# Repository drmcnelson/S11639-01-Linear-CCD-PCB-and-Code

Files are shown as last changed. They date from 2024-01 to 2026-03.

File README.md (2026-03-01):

# S11639-01-Linear-CCD-PCB-and-Code

By Dr M. C. Nelson, Copyright 2020-2025

Original repository [github.com/drmcnelson/S11639-01-Linear-CCD-PCB-and-Code](https://github.com/drmcnelson/S11639-01-Linear-CCD-PCB-and-Code)

This repo provides electronics, firmware and host software for the Hamamatsu S11639-01, a linear CCD sensor that has high sensitivity at 1300V/lx s and low dark noise at 0.2mV (for a 10msec exposure).  With saturation at 2V, the dynamic range is 10,000.
The electrical design is implemented as a two board set, sensor and controller, for mechanical stability and interchangeability.
The sensor board has the socketed sensor, logic gates to drive the pins, and a low noise all differential analog section with a high precision differential 16 bit ADC.
The controller operates the sensor and interacts with a host computer over USB, and has pins for trigger, gate, sync and busy signals.
The command interface is human readable ascii, data transfers are selectable in ascii or binary.

N.B.  This is an update to bring the S11639-0 board into compatibility with the new connector layout for our controller boards.   This design is not yet built, sponsors are welcome.  Please click the sponsor button at the top of the page.

*The original boards and their matching controllers are in the subdirecty labeled [Rev0Boards](./Rev0Boards).*

This version of the board is designed to be used with either of the our controllers, the [Teensy 4.0 based controller](https://github.com/drmcnelson/SPI-Instrumentation-Controller-T4.0) 
and the [Teensy 4.1 based controller](https://github.com/drmcnelson/SPI-Instrumentation-Controller-T4.1).
In principle, the S11639-01 could be used with a number of different Arduino boards.  After some extensive and detailed testing, we prefer the Teensy 4.x boards.  These have good implementations for 16 bit transfers over SPI and they have 480MHz USB for fast transfers to the host computer.

The firmware, which runs in the controller, provides high end functionality including clocked, triggered, and gated operation.
In the firmware, codes that are specific to the sensor are in a separate c++ file and header.  The "sketch file" implements a command interface and calls the sensor code to do the "work" of collecting frames in various operating modes.  The codes throughout, use the standard Arduino libraries plus a small number of optional register level enhancements for the i.MX RT MCU that provide faster and more constant interrupt latency and SPI transfers with less overhead.

## Sensor board details
The following image shows the circuit side of the sensor board with the high precision low noise differential front end (dual opamp lower right, adjacent to the video out pin from the sensor) interfaced to a differential 16bit 1MSPS ADC, and logic level converters (center) for the external digital interface.
The sensor is socketed on the reverse side. 
SPI and logic signals are brought to the double row header at the top edge of the board (ribbon cable compatible).
The external logic level is set by VDD supplied by the controller card.
Power for the sensor and other circuit elements is 5V and supplied by a separate connector.
The small jumper top center near the double row header, selects whether the CNVST pin on the ADC is connected to the TRG signal from the sensor or to the host processor.
(The firmware at present assumes the CNVST pin is connected to the MCU.)
The jumper and header (lower left) selects the internal 4.096V reference or provides a connector for an external reference.
The output from the analog section is available on the three pin header center bottom.
The trim pot should be set to 1.6V for sensors meeting the "typical" spec with output from 0.6V to 2.6V, there is a test point next to the trim pot labeled Voffset where the offset voltage can be measured.

<p align="center">
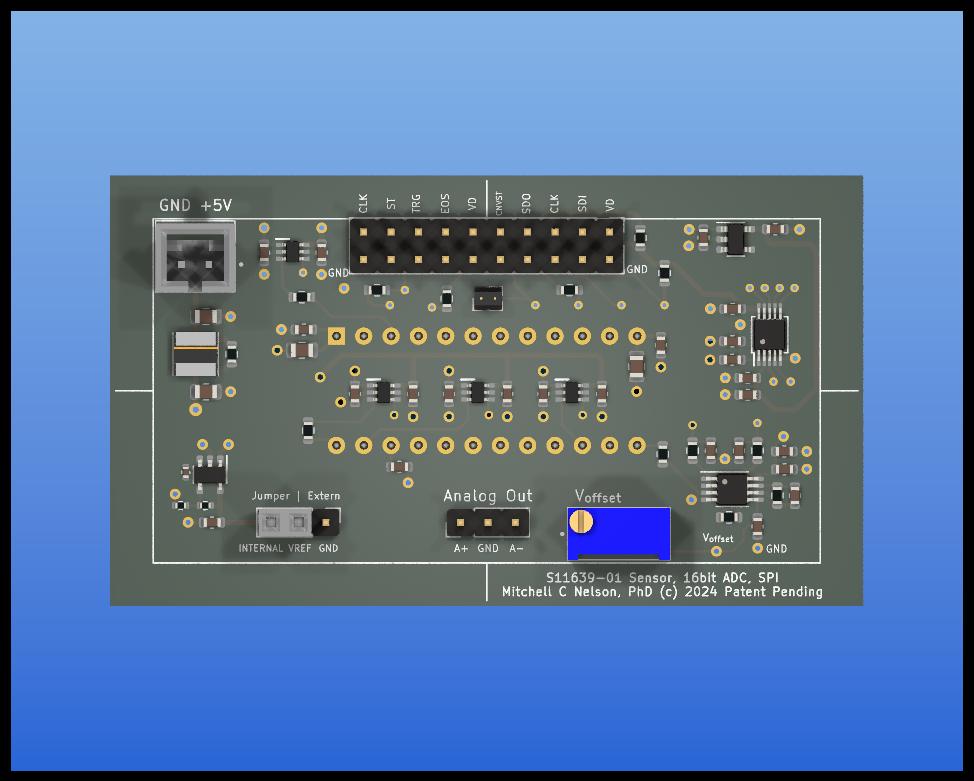
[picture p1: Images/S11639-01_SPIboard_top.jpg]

</p>

<p align="center">
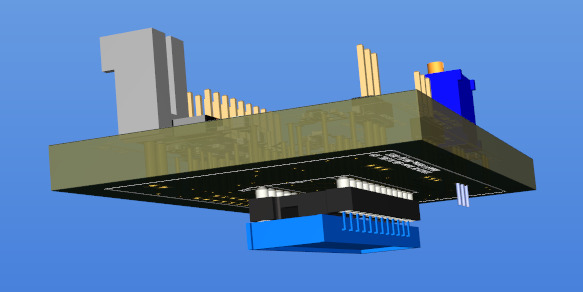
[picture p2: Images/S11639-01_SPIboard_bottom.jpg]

</p>

## T4.0 Controller board details
Please refer to the repo at 
The following describes the T4.0 based controller. The double row header across the top matches that on the sensor board.  The two boards should be connected by a ribbon cable that can be a few inches in length, and by a two wire cable for power, between the connectors labeled "5V" upper left on this board and upper left on the sensor board.  (The power cable will cross over the ribbon cable when the boards are positioned correctly and joined by a ribbon cable.)
The single row headers provides access to the digital interface signals and provides additional pins to the right for a trigger input, sync and busy ouputs and spare digital I/O pin.   The double row header on the left provides access to the onboard analog digital converters and any of these can be used for digitial I/O.  While all of these have diode protection, users should be cognizant that the Teensy is not 5V tolerant. 

<p align="center">
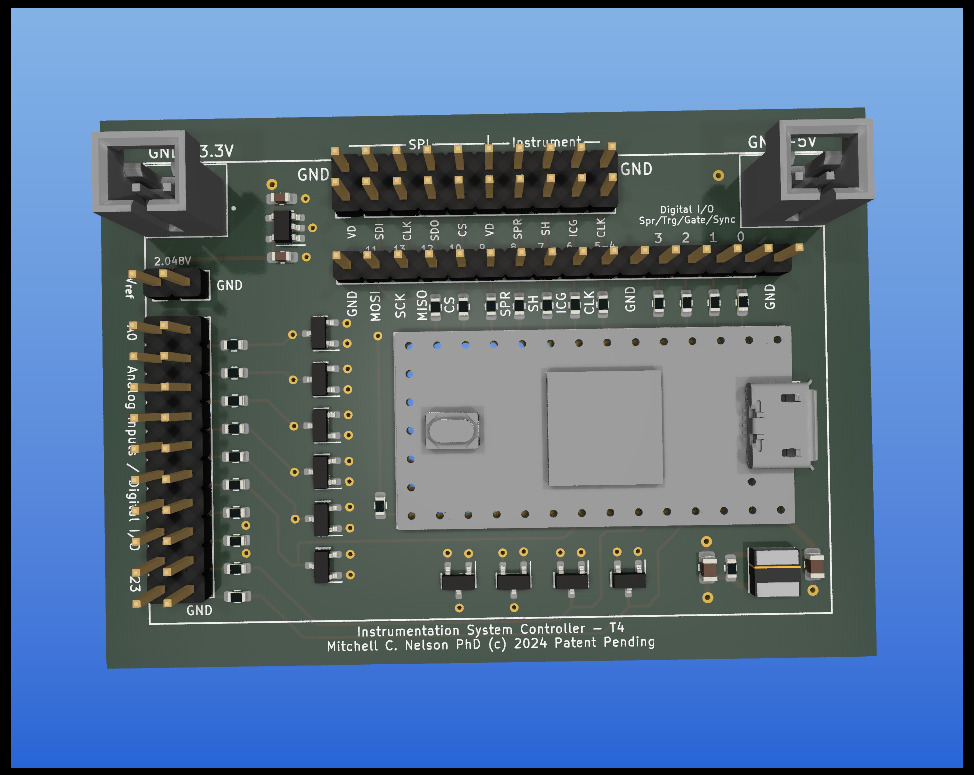
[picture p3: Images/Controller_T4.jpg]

</p>

Running the supplied sketch (see the Firmware directory), the controller appears as a serial port or com port with a human readable command interface.  There is a help command that produces a listing of all of the available commands.  The device can collect (a) single frames, (b) clocked series of frames, (c) triggered single frames, (d) triggered sets of clocked frames (i.e. triggered kinetic series), and (e) gated frames.  There are commands to set the sense (hi/low) of the trigger input and each of the digital outputs, and to set whether the sync output is asserted at the beginning of each frame or series.  There is a "hold off" that can be used to triggered an external device and then wait for a fixed time before collecting a frame.  Busy is asserted whenever the device is active and until data has been transferred to the host computer.   A Python utility and class library and a C language utility and library provide two options for working with the device and integrating into equipment and experiments 

## T4.1 Controller board details
The Teensy 4.1 controller is similar to the T4.0 version, but with more connectors.
In the following image, the long connector across the top corresponds to the 20 connector in the T4.0 controller.  This where the CCD connects. 
Filtered +5V power comes from the connector on the lower right.
The keyed connectors on the left, top and bottom are SPI interfaces 0 and 1.
Analog inputs are to the right of the SPI1 connector
Trigger, sync and busy are implemented in firmware on pins 0, 1, and 2.  These are brought out to a the double row header upper right, so that each pin has a ground pin.
The single row headers provide monitoring points and extended set of digital I/O pins.

<p align="center">
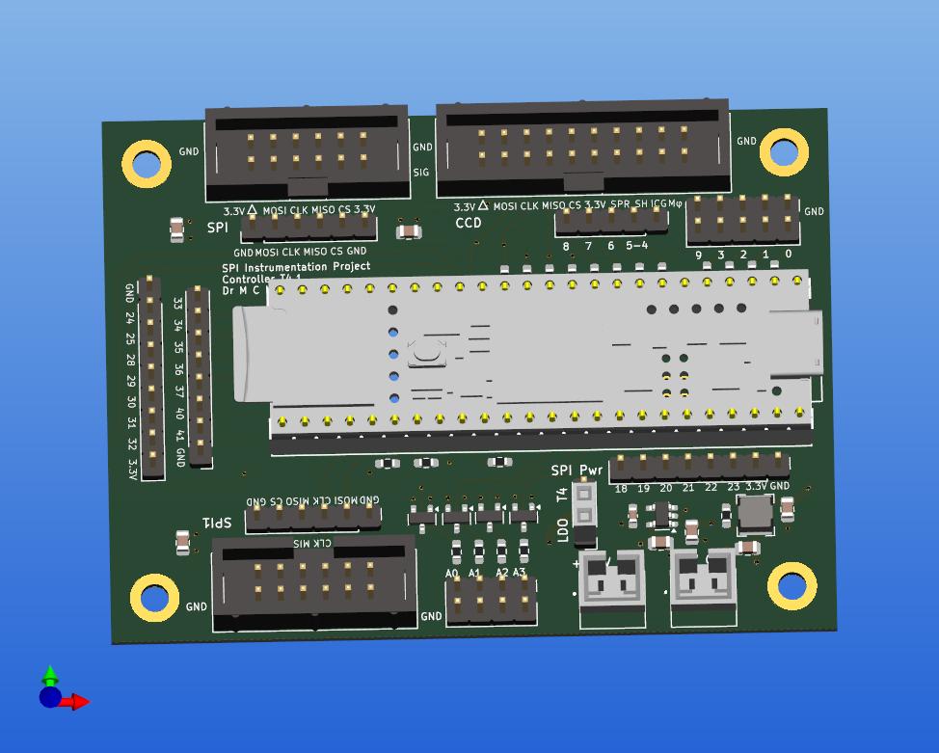
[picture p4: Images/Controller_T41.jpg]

</p>

## Example Spectrometer
The following shows a spectrometer built with the S11639-0 and a fluorescent lamp spectrum collected through an optical fiber and 200um slit and single 100ms exposure, with the fluorescent ceiling lamp at a distance of about 2 meters from the end of the fiber.  (At a 10ms exposure the background is 0.5mV as listed in the datasheet for the sensor.) The sensor board is mounted in a frame that allows adjustment to position the sensor on the focus.  The control board is mounted outside on the light tight cover, for easy access to the pins without disturibing the sensor board, and connected to the sensor board via a 5 inch long ribbon cable and power (twisted red and black wires). Notice that all of the optical mounts are 3-d printed.  The base plate was purchased on Amazon, the sma905 port, slit and lenses on ebay and the transmission grating from Thorlabs.

<p align="center">


</p>
<p align="center">

</p>

## Availability and Sponsorhip
This repo and its contents are provided without warranty or representation of suitability for any purpose whatsoever.

Feel free to build this for your own use or in your lab.  The intent is to support access to doing good science for those who are not as well funded as others.  Commercial use is subject to review and approval, per this criterion.

If you would like a preassembled board, please consider sponsoring and please contact me so that I can get a current cost of materials.

Sponsorship is very much appreciated.  Please click the sponsor button and help us make this and more devices available and support our effort to make doing science more accessible.

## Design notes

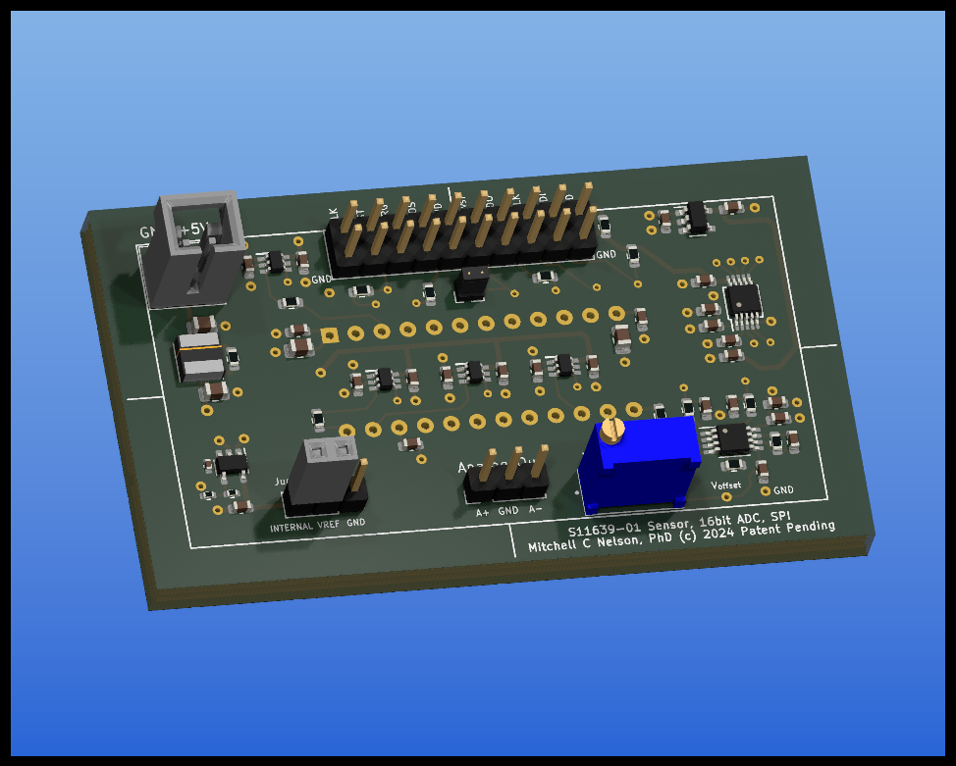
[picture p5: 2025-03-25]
Images/S11639-01_SPIboard_top.png

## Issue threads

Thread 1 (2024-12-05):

### ISSUE TITLE
How to control S11639 bare board

### ISSUE THREAD

**Issue by 9xiaolaji30** [drmcnelson/S11639-01-Linear-CCD-PCB-and-Code#1]
Hello Doctor, I bought a Hamamatsu CMOS (S11639) with only a bare board. Now I need to drive it to output the correct video signal. First, I control the CLK signal and ST signal according to the technical manual, but the output of the video signal is only a few hundred millivolts, and the stronger the light intensity, the smaller the signal. This seems to violate the instructions in the technical manual. Can you show me the ST signal and CLK signal you control? If there is an oscilloscope, the waveform will be better. If not, please tell me how you control the ST signal and CLK signal. Thank you very much! Dear M C Nelson, PhD,

**Comment by drmcnelson** [comment]
Hi,  this is not actually an issue with anything I posted.   You are asking me about the board that you purchased.  Please send me a private note and schematics for what you bought.

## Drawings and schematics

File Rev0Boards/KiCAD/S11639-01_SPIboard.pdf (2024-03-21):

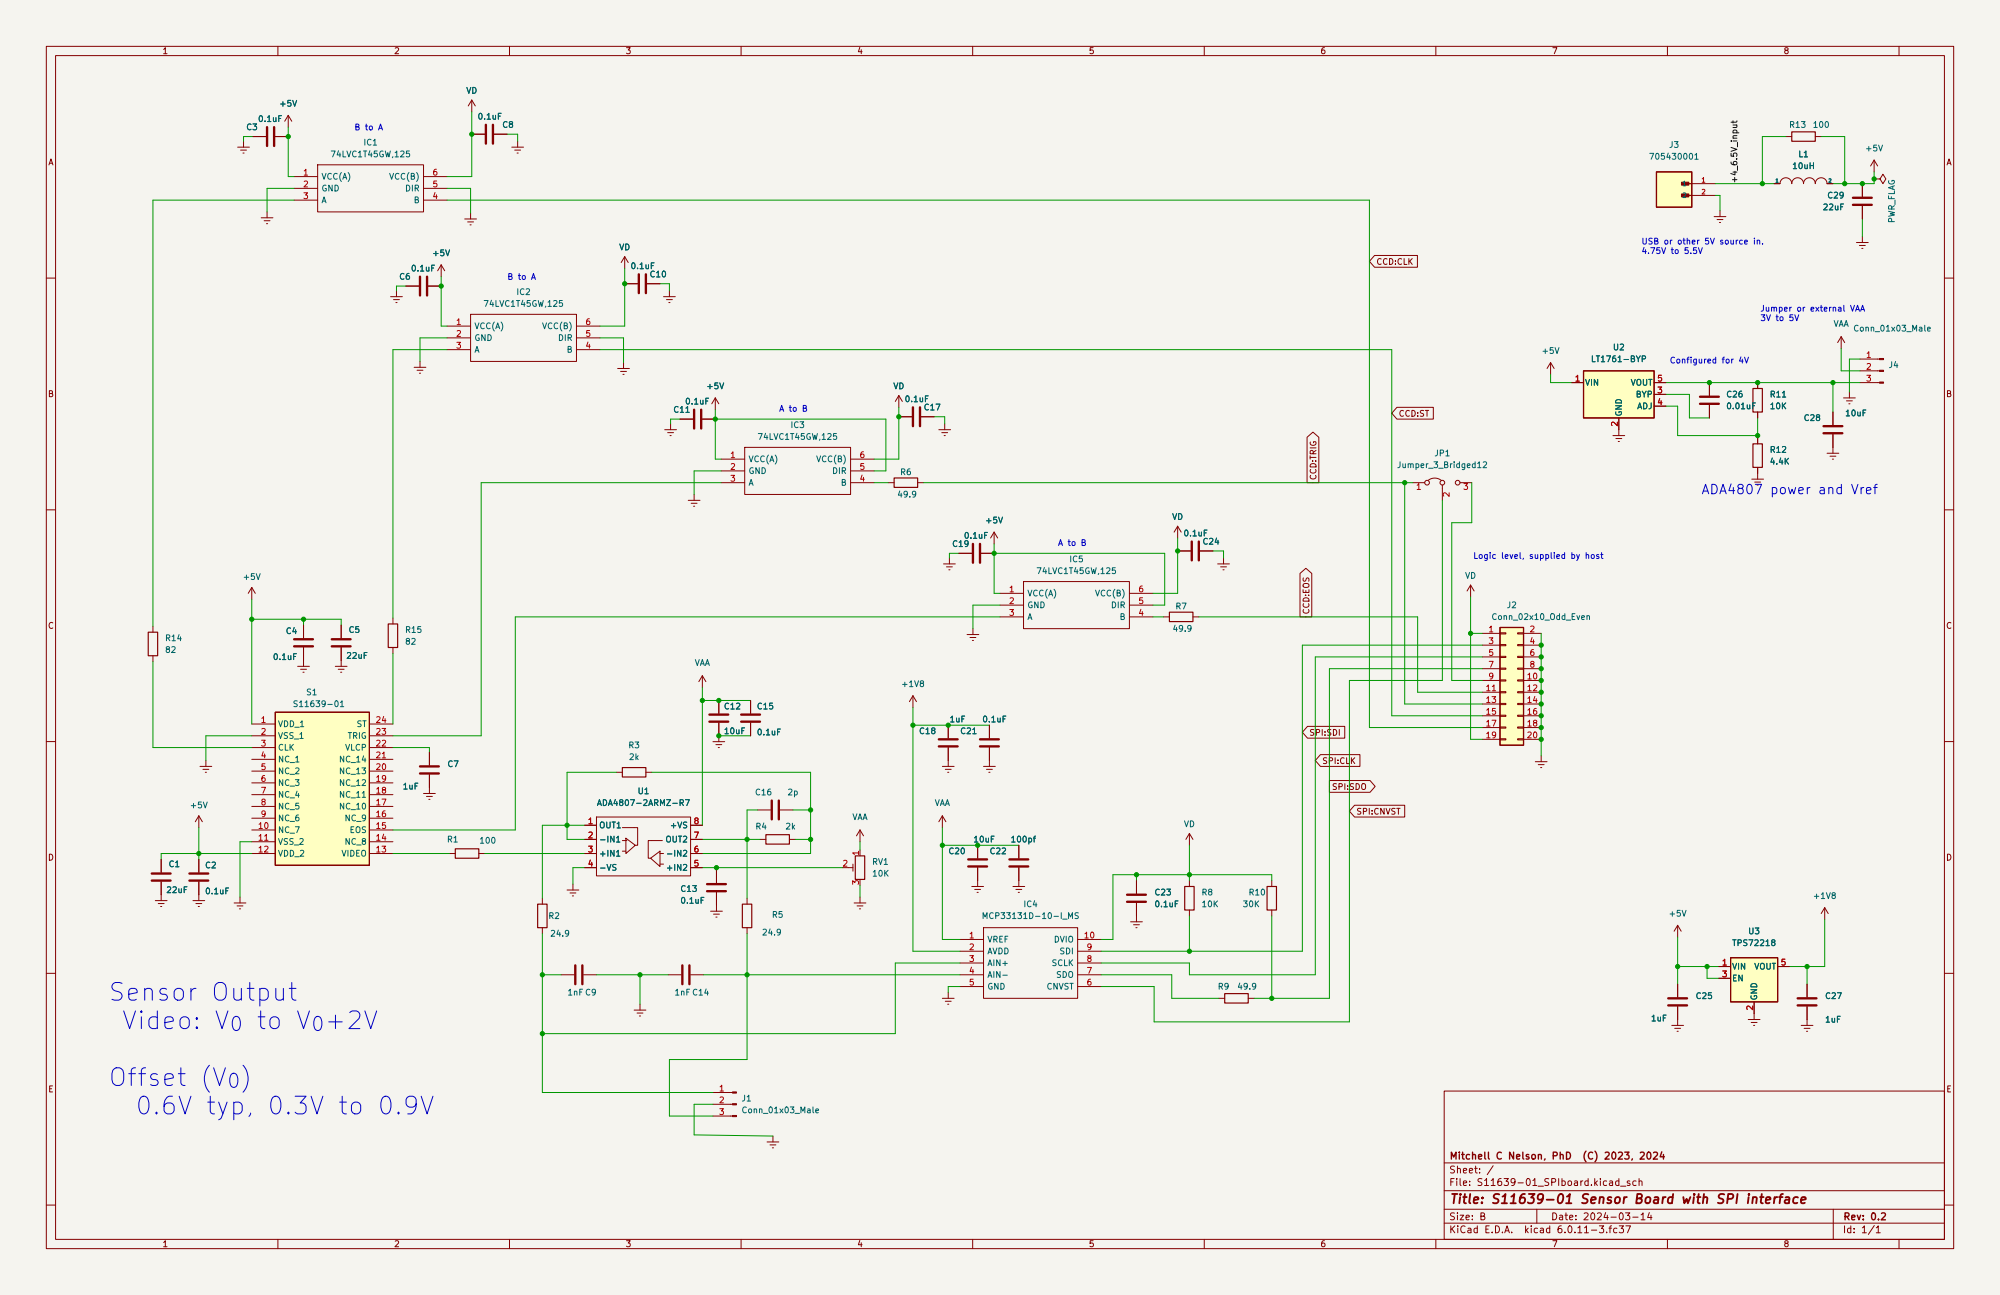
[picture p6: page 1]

USB or other 5V source in. 4.75V to 5.5V

9 | 10
11 | 12
13 | 14
15 | 16
17 | 18
19 | 20

SPI:CNVST SPI:CLK

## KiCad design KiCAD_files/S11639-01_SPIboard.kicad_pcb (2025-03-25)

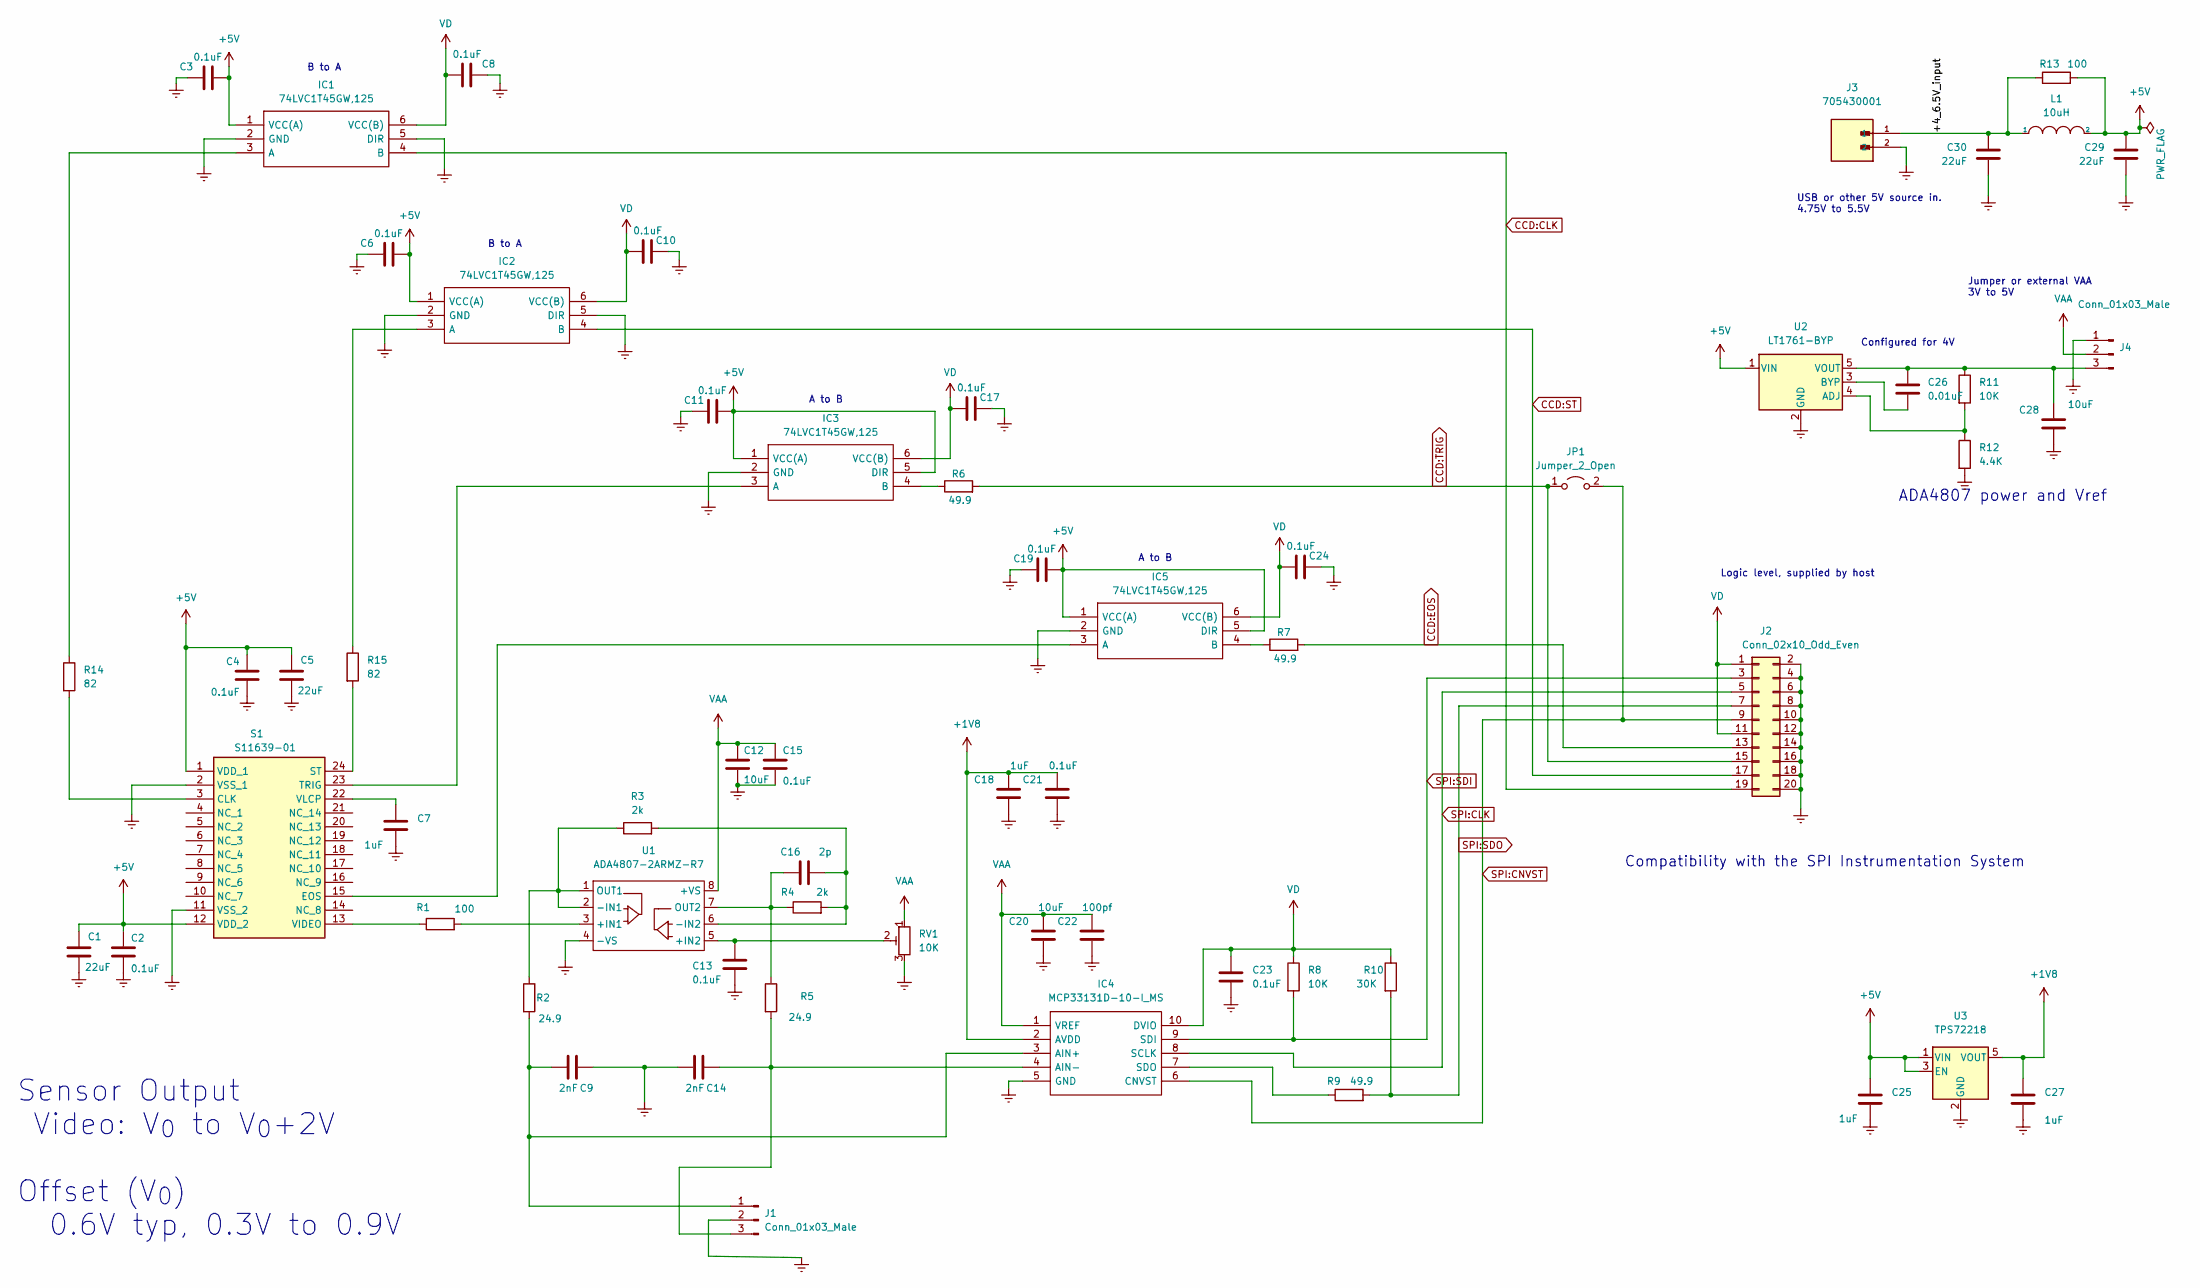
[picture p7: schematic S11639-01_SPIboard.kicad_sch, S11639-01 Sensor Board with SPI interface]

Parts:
C1, C5, C29, C30: 22uF; C_0805_2012Metric; Digikey 311-1903-1-ND
C2, C3, C4, C6, C8, C10, C11, C13, C15, C17, C19, C21, C23, C24: 0.1uF; C_0603_1608Metric; Digikey 445-5666-1-ND
C7, C18, C25, C27: 1uF; C_0603_1608Metric; Digikey 490-10673-1-ND
C9, C14: 2nF; C_0603_1608Metric; Digikey 311-1743-1-ND
C12, C20, C28: 10uF; C_0603_1608Metric; Digikey 490-18214-1-ND
C16: 2p; C_0603_1608Metric; Digikey 311-3827-1-ND
C22: 100pf; C_0603_1608Metric; Digikey 399-17391-1-ND
C26: 0.01uF; C_0402_1005Metric; Digikey 311-1337-1-ND
IC1, IC2, IC3, IC5: 74LVC1T45GW,125; SOT65P210X110-6N; Manufacturer_Part_Number 74LVC1T45GW,125; Digikey 1727-4560-1-ND
IC4: MCP33131D-10-I_MS; MSOP-10_3x3mm_P0.5mm; Manufacturer_Part_Number MCP33131D-10-I/MS; Mouser Part Number 579-MCP33131D10IMS
J1, J4: Conn_01x03_Male; PinHeader_1x03_P2.54mm_Vertical; Digikey 3M156268-03-ND
J2: Conn_02x10_Odd_Even; PinHeader_2x10_P2.54mm_Vertical; Digikey 3M156308-20-ND
J3: 705430001; MOLEX_705430001; PARTREV M1; Digikey WM4800-ND
JP1: Jumper_2_Open; PinHeader_1x02_P1.27mm_Vertical; Digikey S9014E-02-ND
L1: 10uH; L_Taiyo-Yuden_NR-40xx; Digikey 587-2886-1-ND
R1, R13: 100; R_0603_1608Metric; Digikey RNCP0603FTD100RCT-ND
R2, R5: 24.9; R_0603_1608Metric; Digikey 2019-RK73H1JTTD24R9FCT-ND
R3, R4: 2k; R_0603_1608Metric; Digikey P2.0KDBCT-ND
R6, R7, R9: 49.9; R_0603_1608Metric; Digikey RMCF0603FT49R9CT-ND
R8: 10K; R_0603_1608Metric; Digikey 311-10.0KHRCT-ND
R10: 30K; R_0603_1608Metric; Digikey 311-30.0KHRCT-ND
R11: 10K; R_0402_1005Metric; Digikey A127415CT-ND
R12: 4.4K; R_0402_1005Metric; Digikey YAG4274CT-ND
R14, R15: 82; R_0603_1608Metric; Digikey 311-82.0HRCT-ND
RV1: 10K; TRIM_3296W-1-502LF; Digikey 3296W-103LF-ND
S1: S11639-01; DIP-24_W10.16mm_Socket; Manufacturer_Part_Number S11639-01
U1: ADA4807-2ARMZ-R7; MSOP-8_3x3mm_P0.65mm; Digikey ADA4807-2ARMZ-R7CT-ND
U2: LT1761-BYP; TSOT-23-5; Digikey 505-LT1761ES5-BYP#TRMPBFCT-ND
U3: TPS72218; SOT-23-5; Digikey 296-12523-1-ND

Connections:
+1V8: C18.1, C21.1, C27.1, IC4.2 (AVDD), U3.5 (VOUT)
+5V: C1.1, C2.1, C3.1, C4.1, C5.1, C6.1, C11.1, C19.1, C25.1, C29.1, IC1.1 (VCC(A)), IC2.1 (VCC(A)), IC3.1 (VCC(A)), IC3.5 (DIR), IC5.1 (VCC(A)), IC5.5 (DIR), L1.2, R13.2, S1.1 (VDD_1), S1.12 (VDD_2), U2.1 (VIN), U3.1 (VIN), U3.3 (EN)
/+4_6.5V_input: C30.1, J3.1, L1.1, R13.1
CCD:CLK: IC1.4 (B), J2.19
CCD:EOS: J2.13, R7.2
CCD:ST: IC2.4 (B), J2.17
CCD:TRIG: J2.15, JP1.1 (A), R6.2
Earth: C1.2, C2.2, C3.2, C4.2, C5.2, C6.2, C7.2, C8.2, C9.1, C10.2, C11.2, C12.2, C13.2, C14.2, C15.2, C17.2, C18.2, C19.2, C20.2, C21.2, C22.2, C23.2, C24.2, C25.2, C27.2, C28.2, C29.2, C30.2, IC1.2 (GND), IC1.5 (DIR), IC2.2 (GND), IC2.5 (DIR), IC3.2 (GND), IC4.5 (GND), IC5.2 (GND), J1.2, J2.2, J2.4, J2.6, J2.8, J2.10, J2.12, J2.14, J2.16, J2.18, J2.20, J3.2, J4.1, R12.2, RV1.3, S1.2 (VSS_1), S1.11 (VSS_2), U1.4 (-VS), U2.2 (GND), U3.2 (GND)
unnamed: IC1.3 (A), R14.1
unnamed: IC2.3 (A), R15.1
unnamed: IC3.3 (A), S1.23 (TRIG)
unnamed: IC3.4 (B), R6.1
unnamed: C9.2, IC4.3 (AIN+), J1.1, R2.2
unnamed: C14.1, IC4.4 (AIN-), J1.3, R5.2
unnamed: IC4.7 (SDO), R9.1
unnamed: IC5.3 (A), S1.15 (EOS)
unnamed: IC5.4 (B), R7.1
unnamed: C26.1, C28.1, J4.3, R11.1, U2.5 (VOUT)
unnamed: R14.2, S1.3 (CLK)
unnamed: R15.2, S1.24 (ST)
unnamed: R1.1, S1.13 (VIDEO)
unnamed: C7.1, S1.22 (VLCP)
unnamed: R1.2, U1.3 (+IN1)
unnamed: C13.1, RV1.2, U1.5 (+IN2)
unnamed: R2.1, R3.1, U1.1 (OUT1), U1.2 (-IN1)
unnamed: C16.2, R3.2, R4.2, U1.6 (-IN2)
unnamed: C16.1, R4.1, R5.1, U1.7 (OUT2)
unnamed: R11.2, R12.1, U2.4 (ADJ)
unnamed: C26.2, U2.3 (BYP)
SPI:CLK: IC4.8 (SCLK), J2.5
SPI:CNVST: IC4.6 (CNVST), J2.9, JP1.2 (B)
SPI:SDI: IC4.9 (SDI), J2.3, R8.2
SPI:SDO: J2.7, R9.2, R10.2
VAA: C12.1, C15.1, C20.1, C22.1, IC4.1 (VREF), J4.2, RV1.1, U1.8 (+VS)
VD: C8.1, C10.1, C17.1, C23.1, C24.1, IC1.6 (VCC(B)), IC2.6 (VCC(B)), IC3.6 (VCC(B)), IC4.10 (DVIO), IC5.6 (VCC(B)), J2.1, J2.11, R8.1, R10.1

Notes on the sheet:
B to A
USB or other 5V source in. 4.75V to 5.5V
A to B
Compatibility with the SPI Instrumentation System
Logic level, supplied by host
Jumper or external VAA 3V to 5V
Configured for 4V
ADA4807 power and Vref
Sensor Output Video: V_{0} to V_{0}+2V Offset (V_{0}) 0.6V typ, 0.3V to 0.9V

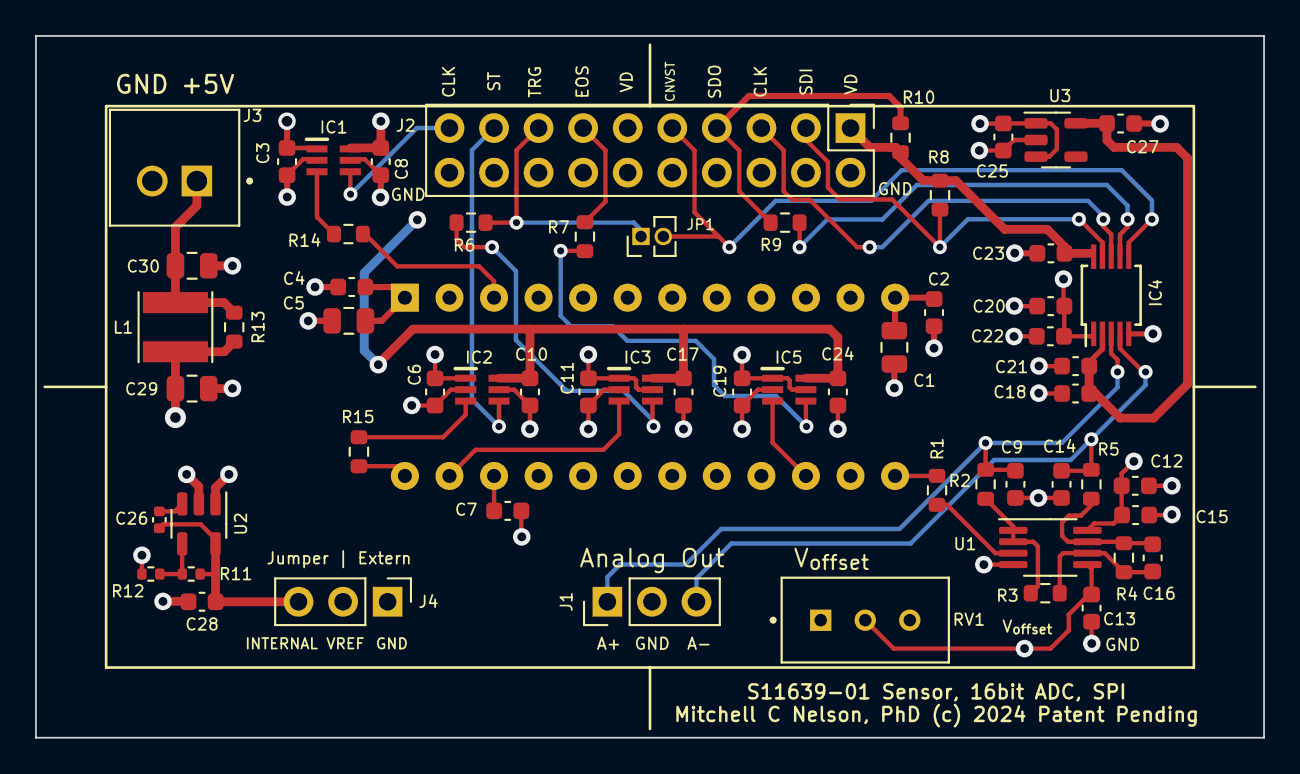
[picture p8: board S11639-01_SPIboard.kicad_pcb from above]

Board: 4 copper layers, 70.0 x 40.0 mm, 61 parts (1 on the bottom side), 35 nets.

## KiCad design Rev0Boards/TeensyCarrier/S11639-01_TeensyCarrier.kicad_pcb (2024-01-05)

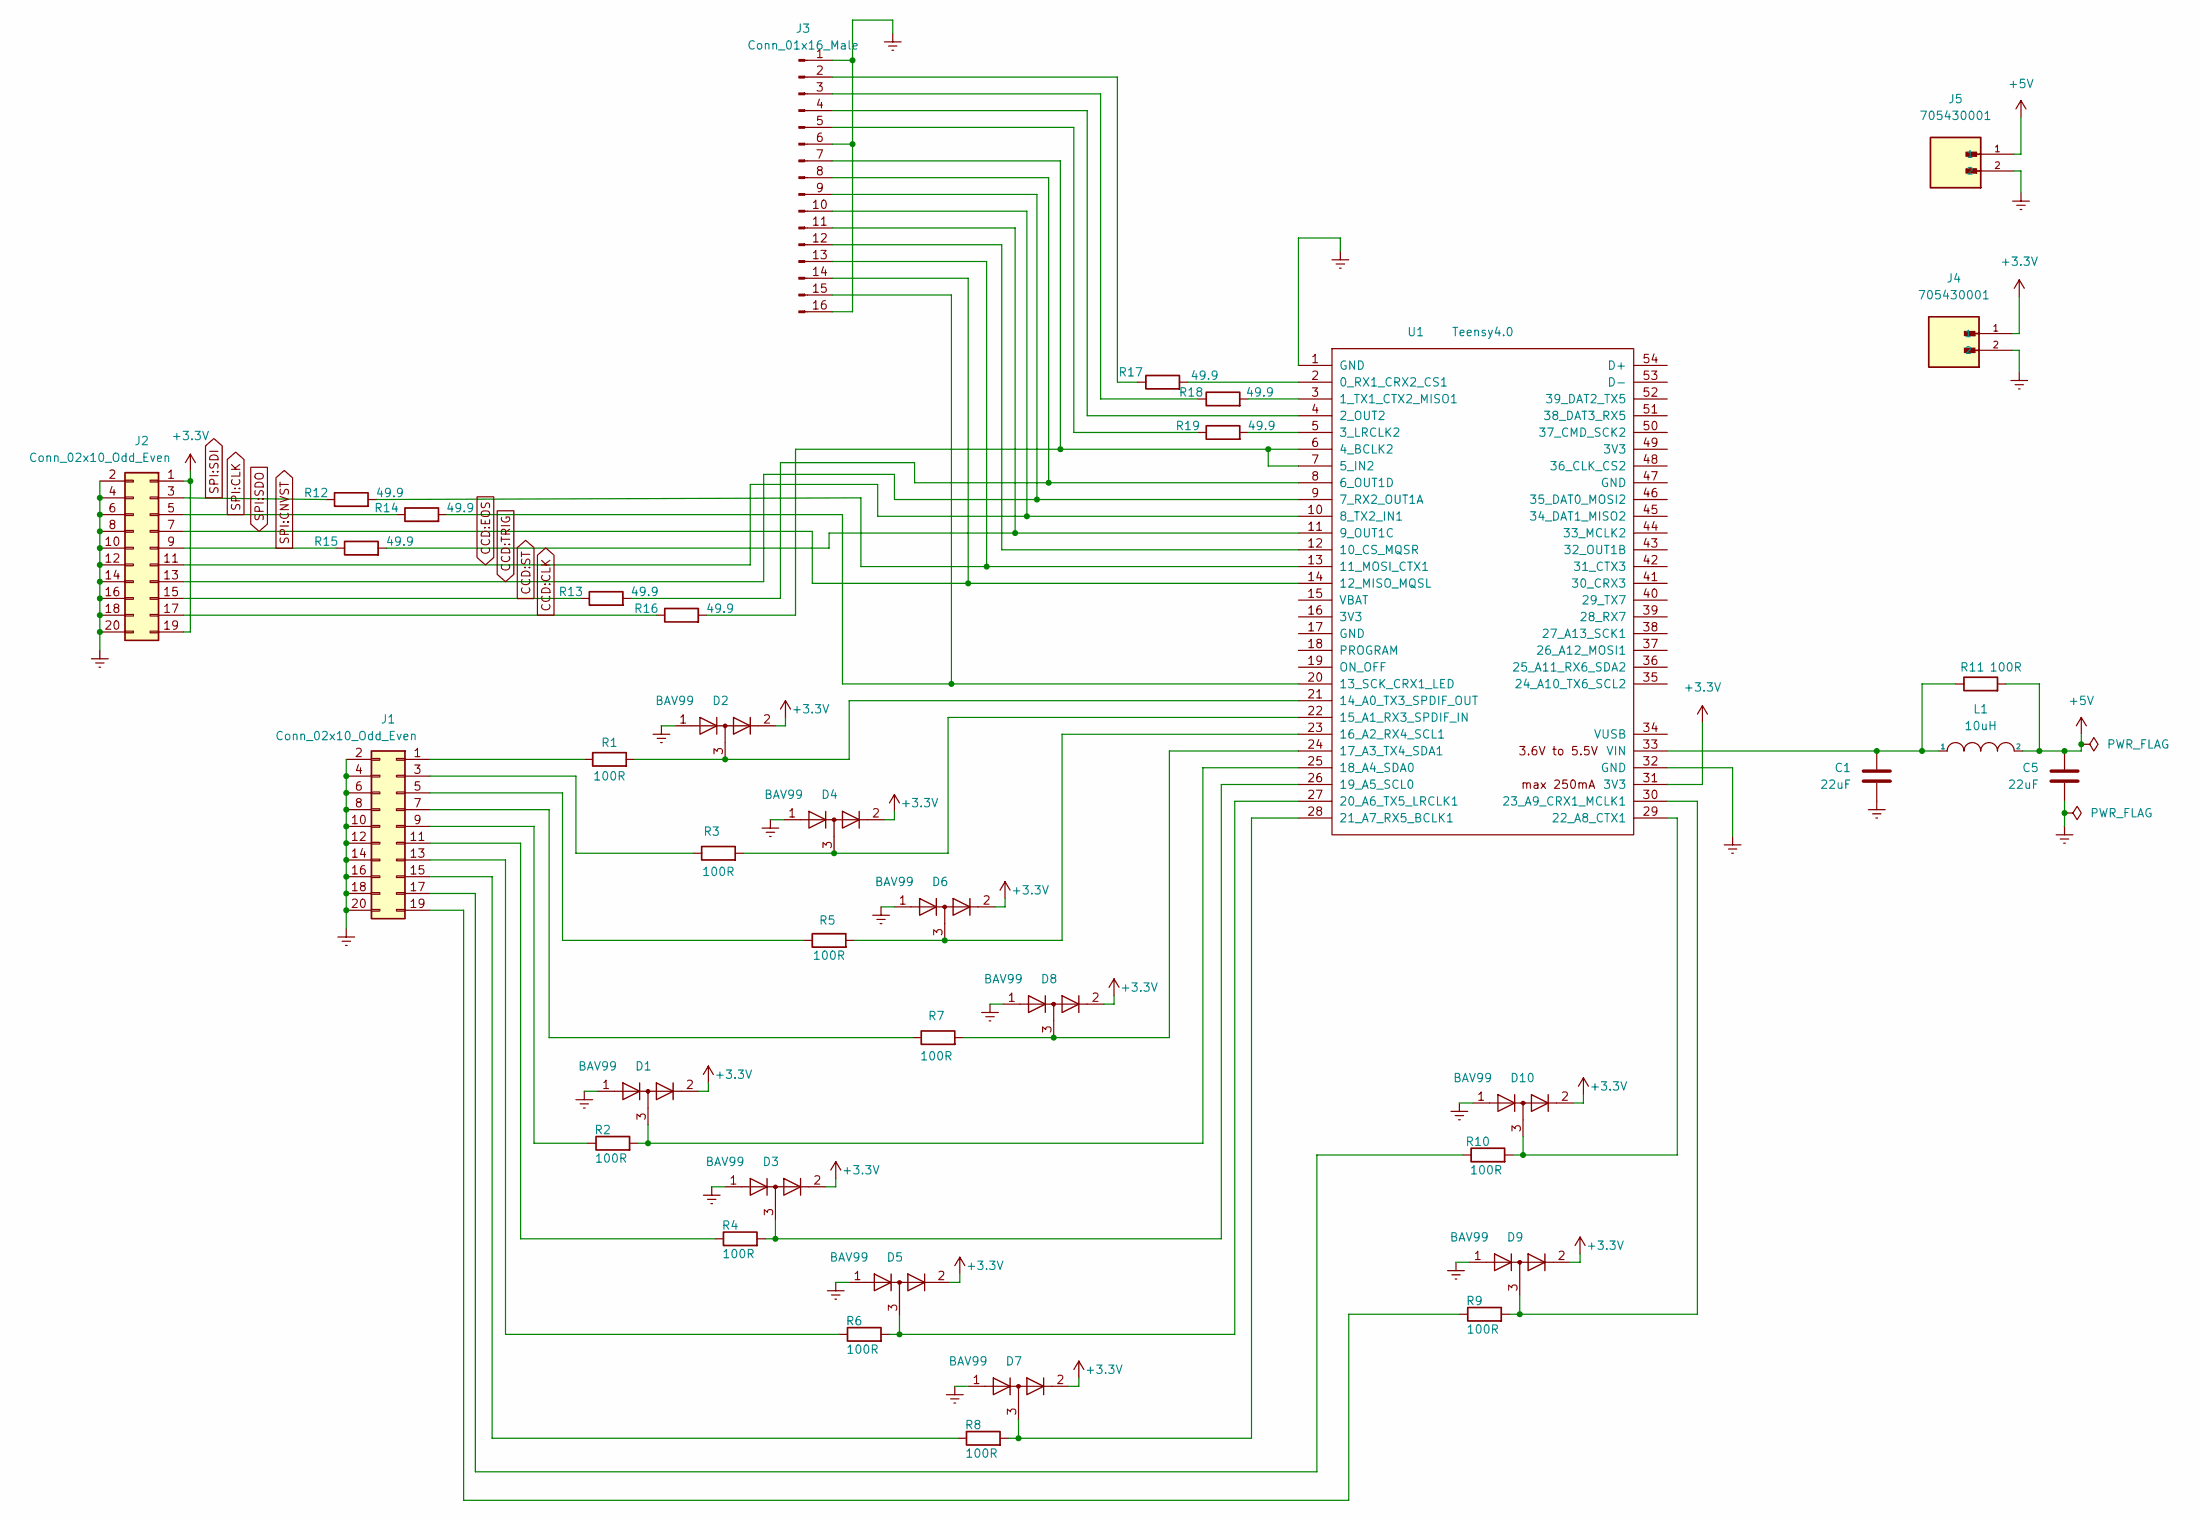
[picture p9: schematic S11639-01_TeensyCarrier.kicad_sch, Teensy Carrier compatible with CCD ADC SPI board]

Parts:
C1, C5: 22uF; C_0805_2012Metric; Digikey 490-12389-1-ND
D1, D2, D3, D4, D5, D6, D7, D8, D9, D10: BAV99; SOT-23; Digikey 1727-2914-1-ND
J1, J2: Conn_02x10_Odd_Even; PinHeader_2x10_P2.54mm_Vertical; Digikey 3M156308-20-ND
J3: Conn_01x16_Male; PinHeader_1x16_P2.54mm_Vertical; Digikey 3M156268-16-ND
J4, J5: 705430001; MOLEX_705430001; PARTREV M1; Digikey WM4800-ND
L1: 10uH; L_Taiyo-Yuden_NR-40xx; Digikey 587-2886-1-ND
R1, R2, R3, R4, R5, R6, R7, R8, R9, R10: 100R; R_0603_1608Metric; Digikey 2019-RK73H1JTTD1000FCT-ND
R11: 100R; R_0603_1608Metric; Digikey 10-ERJ-UP3F1000VCT-ND
R12, R13, R14, R15, R16, R17, R18, R19: 49.9; R_0603_1608Metric; Digikey RMCF0603FT49R9CT-ND
U1: Teensy4.0; Teensy40; Digikey 1568-DEV-16997-ND

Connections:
+3.3V: D1.2 (A), D2.2 (A), D3.2 (A), D4.2 (A), D5.2 (A), D6.2 (A), D7.2 (A), D8.2 (A), D9.2 (A), D10.2 (A), J2.1, J2.19, J4.1, U1.31 (3V3)
+5V: C5.1, J5.1, L1.2, R11.2
CCD:CLK: J2.17, R16.1
CCD:EOS: J2.11, J3.10, U1.10 (8_TX2_IN1)
CCD:ST: J2.15, R13.1
CCD:TRIG: J2.13, J3.9, U1.9 (7_RX2_OUT1A)
Earth: C1.2, C5.2, D1.1 (K), D2.1 (K), D3.1 (K), D4.1 (K), D5.1 (K), D6.1 (K), D7.1 (K), D8.1 (K), D9.1 (K), D10.1 (K), J1.2, J1.4, J1.6, J1.8, J1.10, J1.12, J1.14, J1.16, J1.18, J1.20, J2.2, J2.4, J2.6, J2.8, J2.10, J2.12, J2.14, J2.16, J2.18, J2.20, J3.1, J3.6, J3.16, J4.2, J5.2, U1.1 (GND), U1.32 (GND)
unnamed: C1.1, L1.1, R11.1, U1.33 (VIN)
unnamed: D1.3 (K), R2.2, U1.25 (18_A4_SDA0)
unnamed: D2.3 (K), R1.2, U1.21 (14_A0_TX3_SPDIF_OUT)
unnamed: D3.3 (K), R4.2, U1.26 (19_A5_SCL0)
unnamed: D4.3 (K), R3.2, U1.22 (15_A1_RX3_SPDIF_IN)
unnamed: D5.3 (K), R6.2, U1.27 (20_A6_TX5_LRCLK1)
unnamed: D6.3 (K), R5.2, U1.23 (16_A2_RX4_SCL1)
unnamed: D7.3 (K), R8.2, U1.28 (21_A7_RX5_BCLK1)
unnamed: D8.3 (K), R7.2, U1.24 (17_A3_TX4_SDA1)
unnamed: D9.3 (K), R9.2, U1.30 (23_A9_CRX1_MCLK1)
unnamed: D10.3 (K), R10.2, U1.29 (22_A8_CTX1)
unnamed: J1.1, R1.1
unnamed: J1.3, R3.1
unnamed: J1.5, R5.1
unnamed: J1.7, R7.1
unnamed: J1.9, R2.1
unnamed: J1.11, R4.1
unnamed: J1.13, R6.1
unnamed: J1.15, R8.1
unnamed: J1.17, R10.1
unnamed: J1.19, R9.1
unnamed: J2.3, R12.1
unnamed: J3.2, R17.1
unnamed: J3.3, R18.1
unnamed: J3.4, U1.4 (2_OUT2)
unnamed: J3.5, R19.1
unnamed: J3.7, R16.2, U1.6 (4_BCLK2), U1.7 (5_IN2)
unnamed: J3.8, R13.2, U1.8 (6_OUT1D)
unnamed: J3.11, R15.2, U1.11 (9_OUT1C)
unnamed: J3.12, U1.12 (10_CS_MQSR)
unnamed: J3.13, R12.2, U1.13 (11_MOSI_CTX1)
unnamed: J3.15, R14.2, U1.20 (13_SCK_CRX1_LED)
unnamed: R17.2, U1.2 (0_RX1_CRX2_CS1)
unnamed: R18.2, U1.3 (1_TX1_CTX2_MISO1)
unnamed: R19.2, U1.5 (3_LRCLK2)
SPI:CLK: J2.5, R14.1
SPI:CNVST: J2.9, R15.1
SPI:SDO: J2.7, J3.14, U1.14 (12_MISO_MQSL)

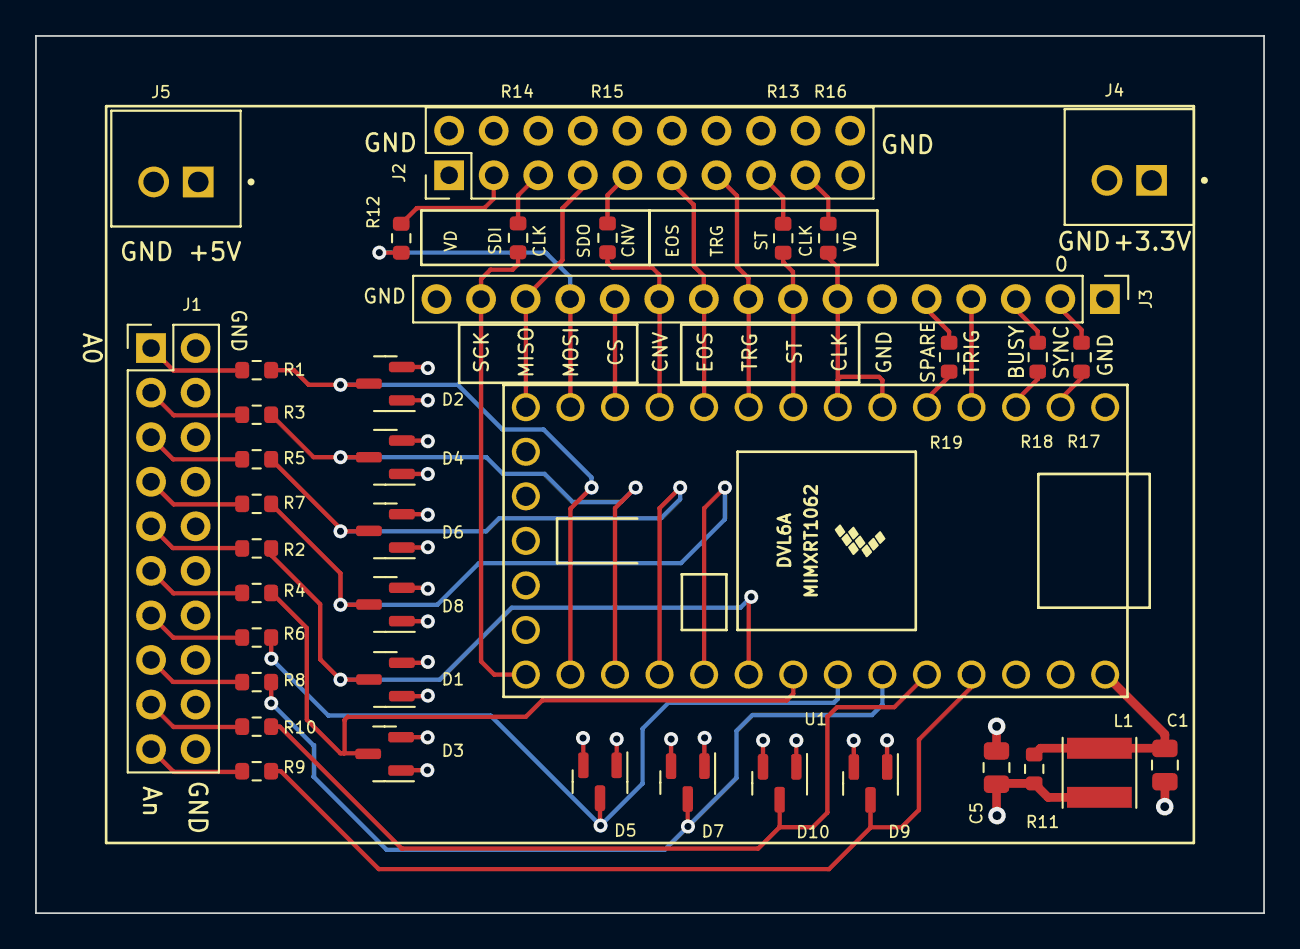
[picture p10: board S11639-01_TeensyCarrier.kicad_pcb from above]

Board: 4 copper layers, 70.0 x 50.0 mm, 38 parts (0 on the bottom side), 45 nets.

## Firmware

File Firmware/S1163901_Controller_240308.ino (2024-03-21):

/*
  Author:   Mitchell C. Nelson
  Date:     January 3, 2023
  Contact:  drmcnelson@gmail.com
  This work is a derivative of the following works:
  
    RAWHIDfirmware.ino   Mitchell C. Nelson,  June 18, 2021

    TCD1304_201223.ino   Mitchell C. Nelson,  Aug 10 through Dec 23, 2020


  Permissions:

     Permission is hereby granted for non-commercial use.

     For commerical uses, please contact the author at the above email address.

  Provisos:

  1) No representation is offered or assumed of suitability for any purposee whatsoever.

  2) Use entirely at your own risk.

  3) Please cite appropriately in any work using this code.

 */

// ------------------------------------------------------------------
//#define DIAGNOSTICS_CPU
//#define DIAGNOSTICS_IDLER
//#define DIAGNOSTICS_SYNC
//#define DIAGNOSTICS_GATE
// Stream& dataPort = SerialUSB1;
// ------------------------------------------------------------------

#include "Arduino.h"

//#include <digitalWriteFast.h>

#include <SPI.h>

#include <limits.h>

#include <ADC.h>
#include <ADC_util.h>

#include <EEPROM.h>

#include <LittleFS.h>

#include "stringlib.h"

#include "S1163901_SPI.h"

LittleFS_Program filesys;
bool filesys_ready = false;

extern float tempmonGetTemp(void);

// ADC setup
ADC *adc = new ADC();

#define MAXADC 8
uint8_t adcpins[MAXADC] = { A0, A1, A2, A3, A4, A5, A6, A7 };

// CPU Cycles per Usec
#define CYCLES_PER_USEC (F_CPU / 1000000)

// Measure elapsed time in cpu clock cycles
uint32_t elapsed_cycles_holder;
inline uint32_t elapsed_cycles() {
  return (ARM_DWT_CYCCNT - elapsed_cycles_holder);
}

inline void elapsed_cycles_start() {
  elapsed_cycles_holder = ARM_DWT_CYCCNT;
}

// Uncomment for Elapsed time in usecs
//elapsedMicros elapsed_usecs;

// ------------------------------------------------------------------

#define thisMANUFACTURER_NAME {'D','R','M','C','N','E','L','S','O','N' }
#define thisMANUFACTURER_NAME_LEN 10

#define thisPRODUCT_NAME {'S','p','e','c','S','1','6','6','3','9','0','1','V','0','1'}
#define thisPRODUCT_NAME_LEN 15
#define thisPRODUCT_SERIAL_NUMBER { 'S','N','0','0','0','0','0','0','0','0','0','1' }
#define thisPRODUCT_SERIAL_NUMBER_LEN 12

extern "C"
{
  struct usb_string_descriptor_struct_manufacturer
  {
    uint8_t bLength;
    uint8_t bDescriptorType;
    uint16_t wString[thisMANUFACTURER_NAME_LEN];
  };

  usb_string_descriptor_struct_manufacturer usb_string_manufacturer_name = {
    2 + thisMANUFACTURER_NAME_LEN * 2,
    3,
    thisMANUFACTURER_NAME
  };

  // -------------------------------------------------
  
  struct usb_string_descriptor_struct_product
  {
    uint8_t bLength;
    uint8_t bDescriptorType;
    uint16_t wString[thisPRODUCT_NAME_LEN];
  };

  usb_string_descriptor_struct_product usb_string_product_name = {
    2 + thisPRODUCT_NAME_LEN * 2,
    3,
    thisPRODUCT_NAME
  };

  // -------------------------------------------------
  
  struct usb_string_descriptor_struct_serial_number
  {
    uint8_t bLength;
    uint8_t bDescriptorType;
    uint16_t wString[thisPRODUCT_SERIAL_NUMBER_LEN];
  };

  usb_string_descriptor_struct_serial_number usb_string_serial_number =
    {
      2 + thisPRODUCT_SERIAL_NUMBER_LEN * 2, 
      3,
      thisPRODUCT_SERIAL_NUMBER
    };
}

// ------------------------------------------------------------------

const char versionstr[] = "T4LCD vers 0.3";

const char authorstr[] =  "Patents Pending and (c) 2024 by Mitchell C. Nelson, Ph.D. ";

void blink() {
  Serial.println( "Error: SPI interface uses the blink ping");
}

/* --------------------------------------------------------
   Extension of the interrupt API, re-enable pin interrupt after dropping pending
 */
#define IMR_INDEX   5
#define ISR_INDEX   6

void resumePinInterrupts(uint8_t pin)
{
	if (pin >= CORE_NUM_DIGITAL) return;
	volatile uint32_t *gpio = portOutputRegister(pin);
	uint32_t mask = digitalPinToBitMask(pin);
        gpio[ISR_INDEX] = mask;  // clear pending
	gpio[IMR_INDEX] |= mask;  // re-enable
}

void disablePinInterrupts(uint8_t pin)
{
	if (pin >= CORE_NUM_DIGITAL) return;
	volatile uint32_t *gpio = portOutputRegister(pin);
	uint32_t mask = digitalPinToBitMask(pin);
	gpio[IMR_INDEX] &= ~mask;
}

/* ===================================================================================================
   External USB command buffer
*/
#define RCVLEN 256
char rcvbuffer[RCVLEN];
uint16_t nrcvbuf = 0;

#define SNDLEN 256
char sndbuffer[SNDLEN];

/* =====================================================================================
   Built-in ADC readout
*/
inline int fastAnalogRead( uint8_t pin ) {
  adc->adc0->startReadFast(pin);
  while ( adc->adc0->isConverting() );
  return adc->adc0->readSingle();
}

/* --------------------------------------------------------
   ADC single reads
   (note that the alpha0 board used the first two channels)
 */
#define NADC_CHANNELS 4
#define ADC_RESOLUTION (3.3/4096.)
uint16_t adc_data[NADC_CHANNELS] = { 0 };

// Set this to something more than 0 to turn on adc reporting.
unsigned int adc_averages = 0;

/* Send ADC readings
 */
void sendADCs( unsigned int averages ) {

  unsigned int i;
  float scalefactor = ADC_RESOLUTION/averages;
  float val;

  int n = averages;

  for( i = 0 ; i < NADC_CHANNELS; i++ ) {
    adc_data[i] = fastAnalogRead( adcpins[i] );
  }
  n--;
  
  while( n-- ) {
    for( i = 0 ; i < NADC_CHANNELS; i++ ) {
      adc_data[i] += fastAnalogRead( adcpins[i] );
    }
  }
  
  Serial.print( "ADCAVGS " );
  Serial.println( averages );
  
  Serial.print( "ADCDATA" );
  for( i = 0 ; i < NADC_CHANNELS; i++ ) {
    val = adc_data[i] * scalefactor;
    Serial.print( " " );
    Serial.print( val, 5 );
  }
  
  Serial.println( "" );
}

/* --------------------------------------------------------
   Send chip temperature
 */

// Set this to something more than 0 to turn on chip temperature reporting
unsigned int chipTemp_averages = 0;

void sendChipTemperature( unsigned int averages ){
  Serial.print( "CHIPTEMPERATURE " );
  Serial.println( tempmonGetTemp() );
}

/* ==========================================================================
   Filesys functions
 */

bool readfromfile( char *name ) {
  File file;
  
  if (!filesys_ready) {
    Serial.println( "Error: filesys not ready" );
    return false;
  }

  if ( !(file = filesys.open( name, FILE_READ )) ) {
    Serial.println( "Error: not able to open for read" );
    return false;
  }

  file.read( (char *) &bufferp[DATASTART], NPIXELS*2 );
  file.close();
  return true;
}

bool writetofile( char *name ) {
  File file;
  
  if (!filesys_ready) {
    Serial.println( "Error: filesys not ready" );
    return false;
  }

  if ( !(file = filesys.open( name, FILE_WRITE_BEGIN )) ) {
    Serial.println( "Error: not able to open for write" );
    return false;
  }

  file.write( (char *) &bufferp[DATASTART], NPIXELS*2 );

  Serial.print( "saved to ");
  Serial.print( file.name() );
  Serial.print( " ");
  Serial.print( NPIXELS*2 );
  Serial.print( " ");
  Serial.println( file.size() );

  file.close();
  
  return true;
}

void listfiles() {
  File dir, entry;
  if (filesys_ready) {
    Serial.print("Space Used = ");
    Serial.println(filesys.usedSize());
    Serial.print("Filesystem Size = ");
    Serial.println(filesys.totalSize());
    dir = filesys.open( "/" );
    while( (entry = dir.openNextFile()) ) {
      Serial.print( entry.name() );
      Serial.print( " " );
      Serial.print( entry.size(), DEC );
      Serial.println();
      entry.close();
    }
    dir.close();
  }
  else {
    Serial.println( "Error: filesys not ready" );
  }
}
  
/* ===================================================================
   Help text
 */
void help() {

  sensor_help();
  
  Serial.println("#Coefficients for pixel number to wwavelength");
  Serial.println("#  store coefficients <a0> <a1> <a2> <a3> (need 4 numbers)");
  Serial.println("#  coefficients       - report");
  Serial.println("#");
  Serial.println("#  store units <string> (upto 6 characters, c.f. nm, um, mm)");
  Serial.println("#  units              - report");
  Serial.println("#");
  Serial.println("#Response function coefficients");
  Serial.println("#  store response <a0> <a1> <a2> <a3>");
  Serial.println("#  response       - report");
  Serial.println("#");
  Serial.println("#Save/recall dark and response spectra");
  Serial.println("#  save dark|resp      - save current buffer as dark or response");
  Serial.println("#  recall dark|resp    - and send it to the host");
  Serial.println("#");
  Serial.println("#  upload int|float    - followed by values one per line from the host");
  Serial.println("#");
  Serial.println("#  save filename       - save from current buffer to internal file");
  Serial.println("#  recall filename     - read from internal file to current buffer and send" );
  Serial.println("#");
  Serial.println("#Identifier string (63 bytes)");
  Serial.println("#  store identifier <identifier>");
  Serial.println("#  identifier         - list identifier string");
  Serial.println("#");
  Serial.println("#Microcontroller functions");
  Serial.println("#  temperature        - report microcontroller temperature");
  Serial.println("#  reboot             - reboots the entire board");
  Serial.println("#");
  Serial.println("#Read and average analog inputs");
  Serial.println("#  adcs <navgs>        - read analog inputs and report");
  Serial.println("#  set adcs <navgs>    - read ADCs at frame completion");
  Serial.println("#  set adcs off");
  Serial.println("#");
}


/* ===================================================================
   The setup routine runs once when you press reset:
*/

void setup() {

  // initialize the digital pin as an output.
#ifdef HASLED
  pinMode(led, OUTPUT);
#endif

  // ------------------------------
  // Setup the onboard ADCs
  adc->adc0->setReference(ADC_REFERENCE::REF_3V3); 
  adc->adc0->setAveraging(1);                 // set number of averages
  adc->adc0->setResolution(12);               // set bits of resolution
  adc->adc0->setConversionSpeed(ADC_CONVERSION_SPEED::HIGH_SPEED); 
  adc->adc0->setSamplingSpeed(ADC_SAMPLING_SPEED::VERY_HIGH_SPEED); 
  adc->adc0->wait_for_cal();  
  adc->adc0->singleMode();              // need this for the fast read

  // ------------------------------
  Serial.begin(9600);
  delay(100);

  // Patent pending and copyright notice displayed at startup
  Serial.println( versionstr );
  Serial.println( authorstr );
  //Serial.println( salesupportstr );

#ifdef DIAGNOSTICS_CPU 
  Serial.print("F_CPU: "); Serial.print(F_CPU/1e6);  Serial.println(" MHz."); 
  //Serial.print("F_BUS: "); Serial.print(F_BUS/1e6);  Serial.println(" MHz."); 
  Serial.print("ADC_F_BUS: "); Serial.print(ADC_F_BUS/1e6); Serial.println(" MHz.");
#endif

  // ------------------------------
  // Linear CCD sensor

  sensor_setup();
  
  // ------------------------------
  // File system in program RAM

#ifdef S1163901_SPI_H
  if (!filesys.begin( 1024*512 ) ) {
    Serial.println( "not able to setup filesys" );
  }
  else {
    filesys_ready = true;
    Serial.println("filesystem ready");
    listfiles();
  }
#endif
  
#ifdef HASLED
  blink();
  delay(1000);
  blink();
#endif

}
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

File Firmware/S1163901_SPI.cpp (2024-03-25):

/*
  Author:   Mitchell C. Nelson
  Date:     March 8, 2024
  Contact:  drmcnelson@gmail.com
  This work is a derivative of the following works:
  
    RAWHIDfirmware.ino   Mitchell C. Nelson,  June 18, 2021

    TCD1304_201223.ino   Mitchell C. Nelson,  Aug 10 through Dec 23, 2020

  Permissions:

     Permission is hereby granted for non-commercial use.

     For commerical uses, please contact the author at the above email address.

  Provisos:

  1) No representation is offered or assumed of suitability for any purposee whatsoever.

  2) Use entirely at your own risk.

  3) Please cite appropriately in any work using this code.

*/

#include "Arduino.h"

//#include <digitalWriteFast.h>
//#include <elapsedMillis.h>  // uncomment this if not Teensy

/* Note self, use this for portability to Arduinos
   
   attachInterrupt( digitalPinToInterrupt( pin_number ), pin_ISR, CHANGE);

*/

#include <SPI.h>

#include <limits.h>

#include <string.h>

#include "S1163901_SPI.h"

#include "eepromlib.h"

//#define TESTING

#define FASTISR
#define FASTSPI

/* =====================================================================
   Fast ISR support
 */

#ifdef FASTISR
#include "imxrt.h"
#include "pins_arduino.h"
#define DR_INDEX    0
#define GDIR_INDEX  1
#define PSR_INDEX   2
#define ICR1_INDEX  3
#define ICR2_INDEX  4
#define IMR_INDEX   5
#define ISR_INDEX   6
#define EDGE_INDEX  7

volatile uint32_t *directgpio;
volatile uint32_t directmask = 0;

inline void directAttach( uint8_t pin, void (*function)(void), int mode ) {
  directgpio = portOutputRegister(pin);
  directmask = digitalPinToBitMask(pin);
  attachInterrupt(pin, function, mode);
  attachInterruptVector(IRQ_GPIO6789, function);
}

inline uint32_t directClear( ) {
  uint32_t status = directgpio[ISR_INDEX] & directgpio[IMR_INDEX];
  if (status) {
    directgpio[ISR_INDEX] = status;
  }
  return status & directmask;
}

void directnoop() {
}

inline void directDetach(uint8_t pin) {
  detachInterrupt(pin);
  attachInterrupt(pin,directnoop,RISING);
  detachInterrupt(pin);
}

#endif

// ==================================================================
// CPU Cycles per Usec
#define CYCLES_PER_USEC (F_CPU / 1000000)

#define NANOSECS_TO_CYCLES(n) (((n)*CYCLES_PER_USEC)/1000)

// ==================================================================
// SPI maximum clock per the ARM7 documents
#define SPI_SPEED 30000000
SPISettings spi_settings( SPI_SPEED, MSBFIRST, SPI_MODE0);   // 30 MHz, reads 1.5usecs/word including CNVST

#define SPI_TO_USECS(nbits) ((nbits*1000)/(SPI_SPEED/1000))
#define USECS_TO_SPI(usecs) ((usecs*(SPI_SPEED/1000))/1000)


//*************************************************************************
// LPSPI helper functions, from KurtE, Teensy4 Forum
#ifdef FASTSPI

IMXRT_LPSPI_t *lpspi = &IMXRT_LPSPI4_S;

uint16_t saved_framesz;

static inline uint16_t get_framesz( IMXRT_LPSPI_t *port ) {
  return (port->TCR & 0x00000fff) + 1;
}

static inline void set_framesz( IMXRT_LPSPI_t *port, uint16_t nbits ) {
  port->TCR = (port->TCR & 0xfffff000) | LPSPI_TCR_FRAMESZ(nbits-1); 
}

static inline uint16_t transfer16( IMXRT_LPSPI_t *port, uint16_t data ) {
  port->TDR = data;                         // output 16 bit data
  while (port->RSR & LPSPI_RSR_RXEMPTY) {}  // wait while RSR fifo is empty
  return port->RDR;                         // return data read
}
#endif

// ==================================================================
// ADC requires 730ns sampling, so this is about as good as it gets
#if defined FASTISR && defined FASTSPI
#define MASTER_CLOCK 660000
#elif defined FASTISR
#define MASTER_CLOCK 600000
#else
#define MASTER_CLOCK 500000
#endif
const unsigned long fM  = MASTER_CLOCK;   // Safe setting, max is 666667 (666.667kHz).
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

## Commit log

2024-03-21 Version 0.2, tested
    Tested, noise is 0.5mV in , per spec for the part. See the firmware directory for an Arduino sketch to use the board. See the Teensy Carrier for a mating board that hosts a Teensy 4.0 to run the sens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
    [S11639-01_SPIboard.kicad_pcb]
2024-03-21 Full feature code to run the sensor board
2025-03-25 upgrade input power filter
    Adds input side cap to the inductive input filter.
    [S11639-01_SPIboard.kicad_pcb, S11639-01_SPIboard.kicad_sch]

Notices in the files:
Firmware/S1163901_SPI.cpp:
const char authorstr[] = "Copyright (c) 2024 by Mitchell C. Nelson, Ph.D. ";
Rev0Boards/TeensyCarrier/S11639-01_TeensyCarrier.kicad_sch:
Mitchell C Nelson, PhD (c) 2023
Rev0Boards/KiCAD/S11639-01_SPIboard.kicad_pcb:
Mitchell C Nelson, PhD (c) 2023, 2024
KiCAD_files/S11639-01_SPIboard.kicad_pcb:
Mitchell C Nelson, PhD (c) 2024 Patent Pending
